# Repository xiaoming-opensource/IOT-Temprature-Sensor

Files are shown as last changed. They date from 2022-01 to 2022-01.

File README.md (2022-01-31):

# 小明开源-物联网温度贴
#采用超小体积BLE和WIFI双模SOC芯片
#完全开源，包括硬件原理图，PCB，外壳，嵌入式源代码等所有

##点击观看视频介绍>>
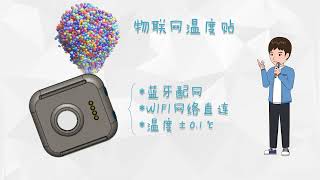
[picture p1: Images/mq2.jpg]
Watch the video (https://youtu.be/xRjZt0CQz3k)


#功能特点如下：

#量度温度，可达医疗级
Medical Level for Measurement of Temperature	
与医疗仪器比较±0.1度摄氏
±0.1℃ compared with Medical Instruments

#通讯功能
Communication	
低功耗WiFi 自动联网
Low Consumption to connect nearby WiFi Automatically
实时数据独立上传
Real Time Transmission

#定位
Location	
佩戴者地点定位
Positioning & Location of the Wearer

#电源
Power Source	
锂电池，可用48小时、磁吸充电
Lithium Battery by Magnetic Charging for use in 48 hours

#后台及小程序
Platform & Applets
实时数据监测
Real Time Data Monitoring
温度异常预警
Alerts of Abnormal Temperatures
实时数据一键分享多人
One-click Sharing of Real Time Data to Unlimited No. of People

#开发环境

#硬件设计
KiCAD
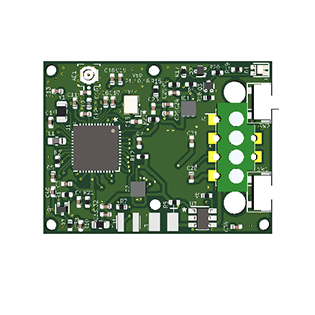
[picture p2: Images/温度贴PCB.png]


#软件设计
Keil uVision5

#外壳设计
Solidworks 2018

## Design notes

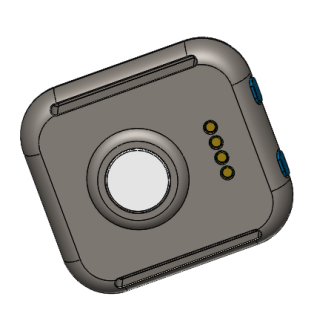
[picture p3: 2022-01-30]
Images/温度贴反面.png

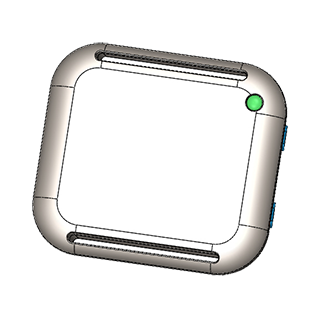
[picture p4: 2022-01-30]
Images/温度贴正面.png

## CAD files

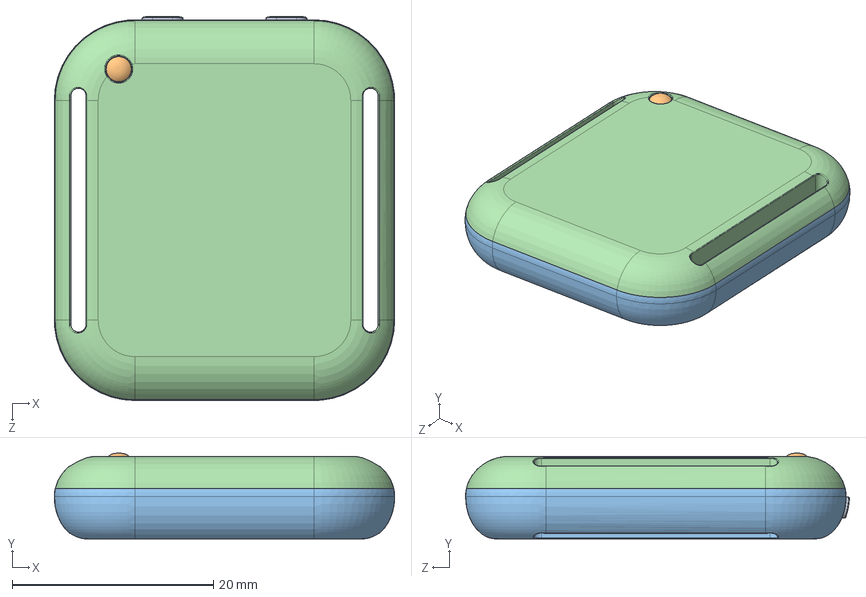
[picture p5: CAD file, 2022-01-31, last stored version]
MechanicalCase/case_v31mz.SLDASM
33.8 x 8.51 x 38.1 mm
button2v30
LED_POLE
body_v31
body_top_v31
battery202025
防水密封圈
popgo_pin_set
IOT-PCBA-v31
top_PAD

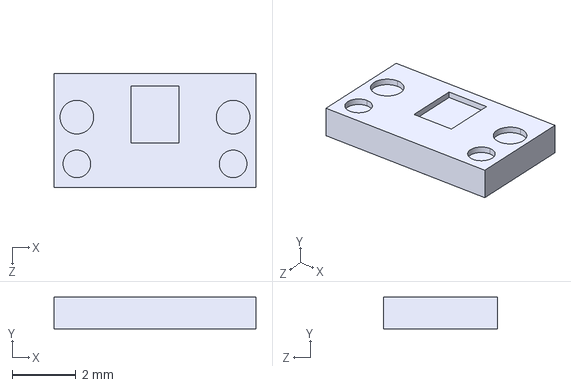
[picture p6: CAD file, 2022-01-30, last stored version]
Hardware/pah8011.STEP
6.36 x 1.00 x 3.60 mm

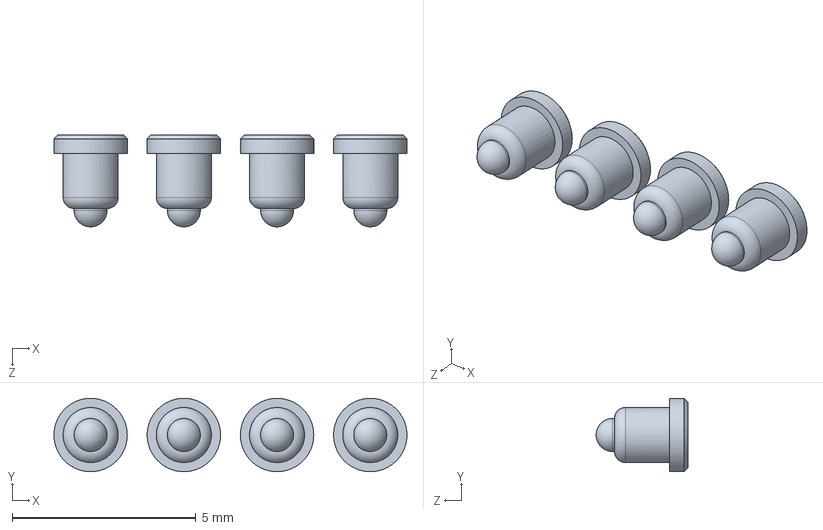
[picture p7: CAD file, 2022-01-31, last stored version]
MechanicalCase/popgo_pin_set.SLDPRT
9.62 x 2.00 x 2.50 mm

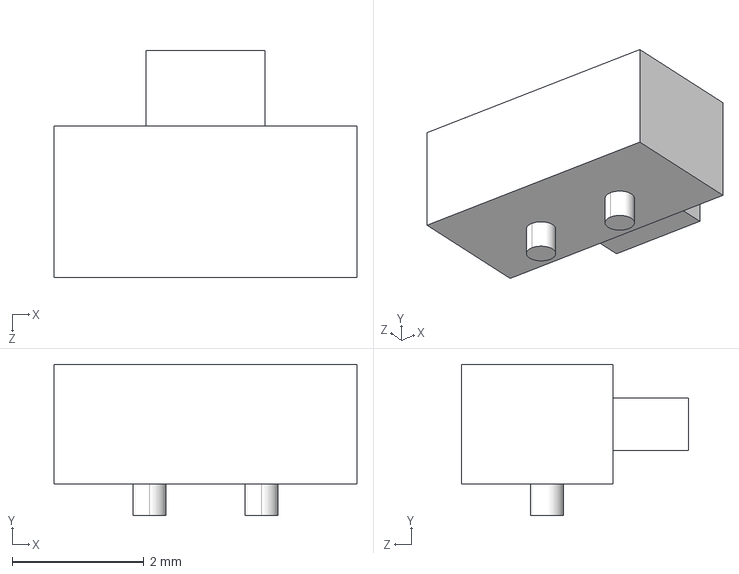
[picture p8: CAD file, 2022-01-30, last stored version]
Hardware/SOS_button.STEP
4.60 x 2.30 x 3.45 mm

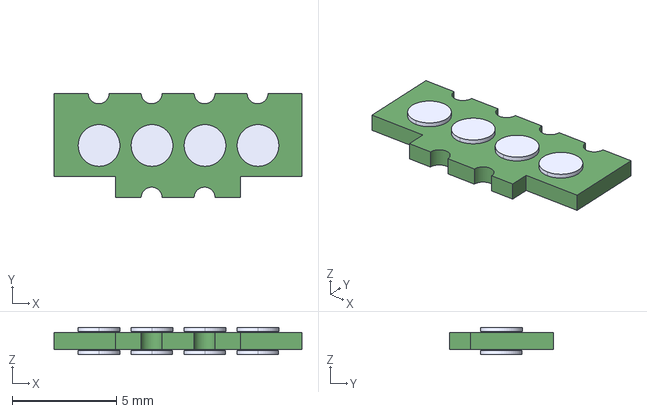
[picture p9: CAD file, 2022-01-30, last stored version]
Hardware/USB_charger.step
11.9 x 5.00 x 1.30 mm

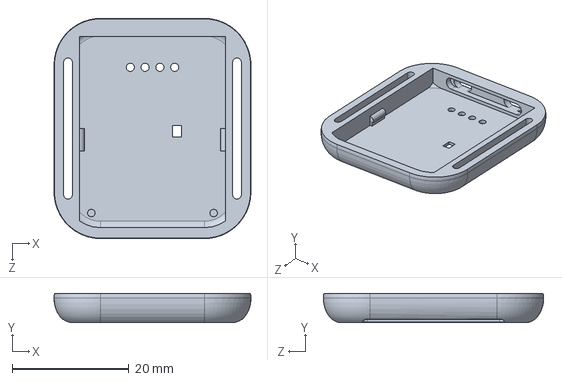
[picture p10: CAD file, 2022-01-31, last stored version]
MechanicalCase/body_v31.SLDPRT
33.8 x 5.00 x 37.8 mm

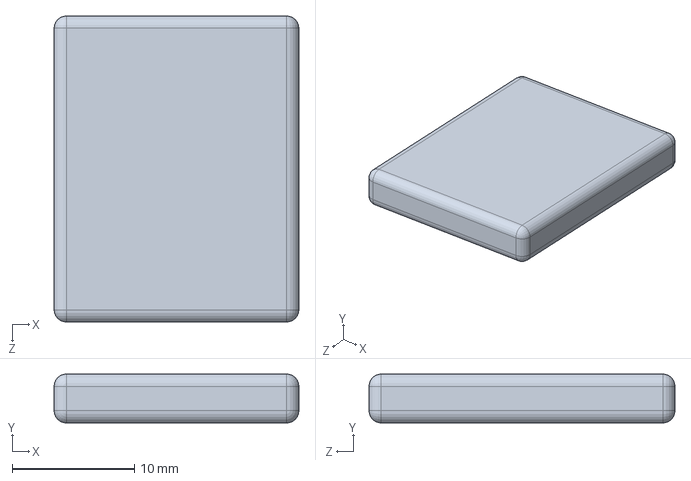
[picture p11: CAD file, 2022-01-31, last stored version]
MechanicalCase/battery202025.SLDPRT
20.0 x 4.00 x 25.0 mm

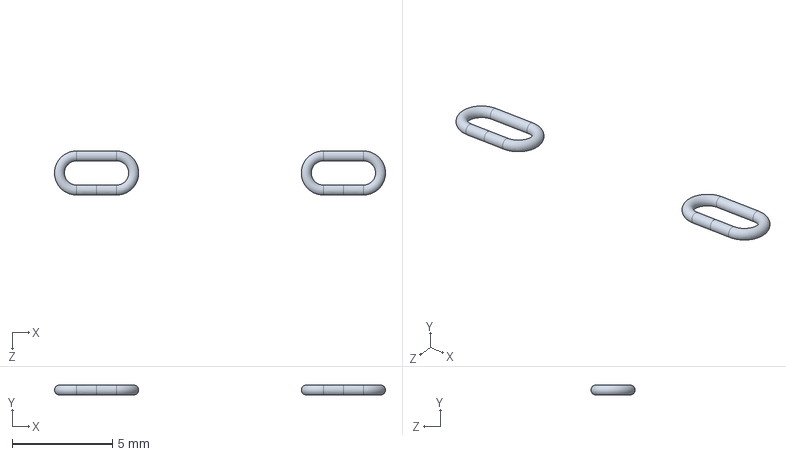
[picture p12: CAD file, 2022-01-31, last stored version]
MechanicalCase/防水密封圈.SLDPRT
16.5 x 0.5 x 2.20 mm

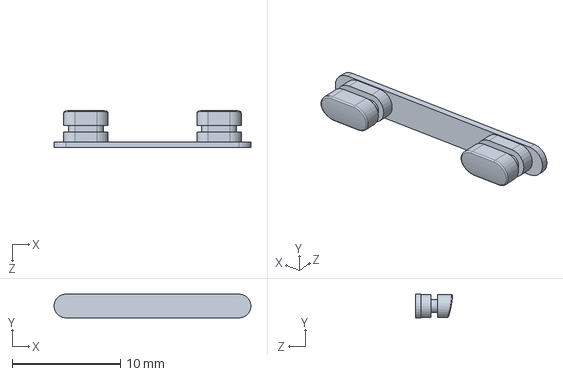
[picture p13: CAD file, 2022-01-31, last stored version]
MechanicalCase/button2v30.SLDPRT
18.2 x 2.20 x 3.43 mm

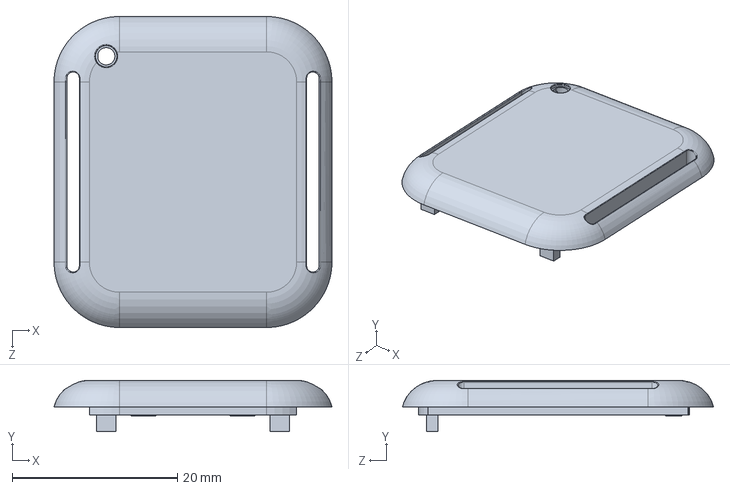
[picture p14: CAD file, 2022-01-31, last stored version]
MechanicalCase/body_top_v31.SLDPRT
33.6 x 6.20 x 37.6 mm

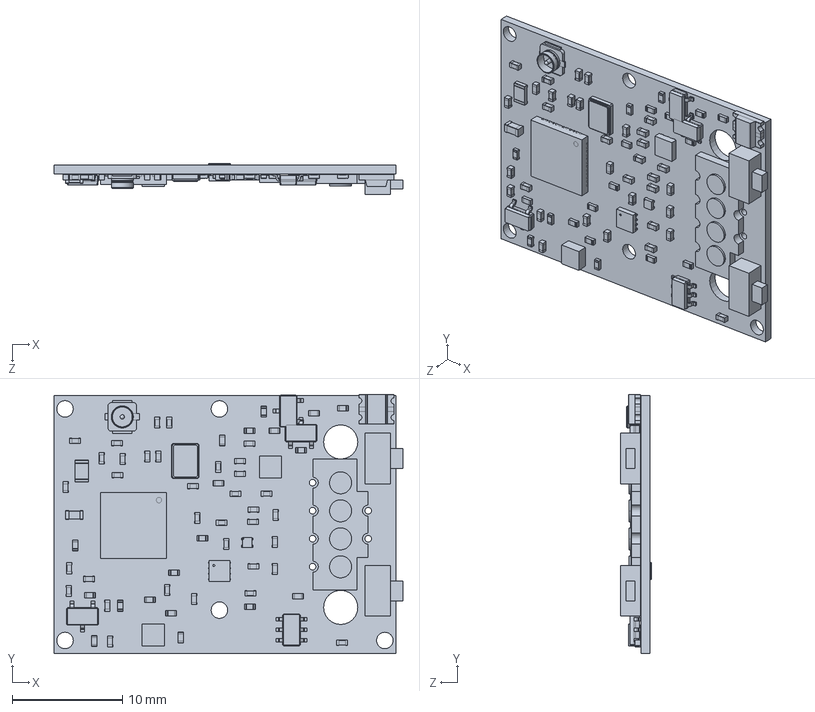
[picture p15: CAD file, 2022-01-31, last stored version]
MechanicalCase/IOT-PCBA-v31.SLDPRT
31.6 x 23.5 x 2.82 mm

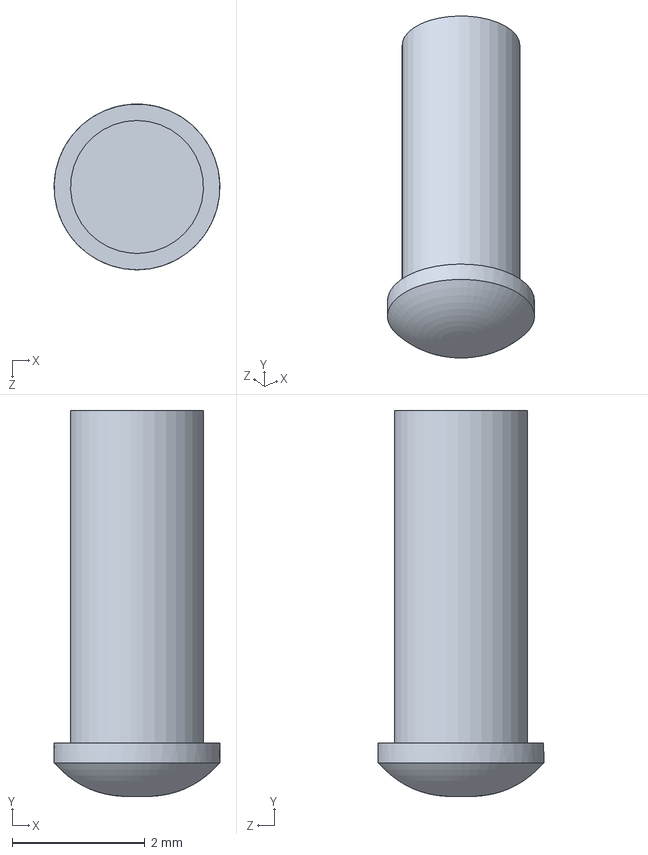
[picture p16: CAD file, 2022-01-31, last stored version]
MechanicalCase/LED_POLE.SLDPRT
2.49 x 5.81 x 2.49 mm

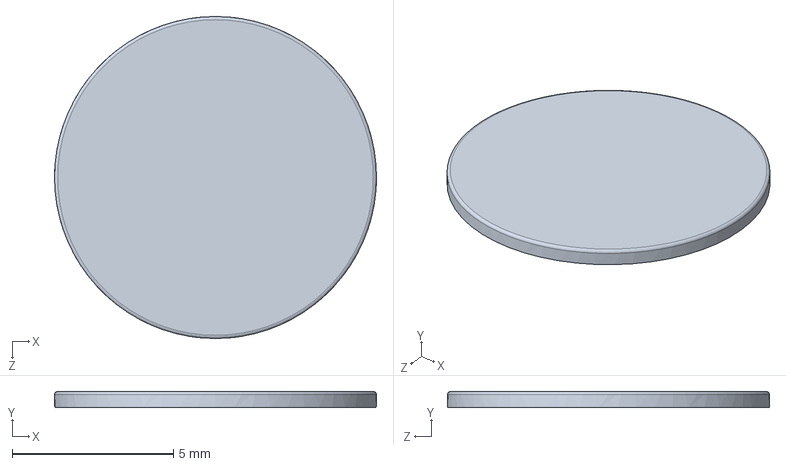
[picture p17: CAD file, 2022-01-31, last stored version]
MechanicalCase/top_PAD.SLDPRT
10.0 x 0.5 x 10.0 mm

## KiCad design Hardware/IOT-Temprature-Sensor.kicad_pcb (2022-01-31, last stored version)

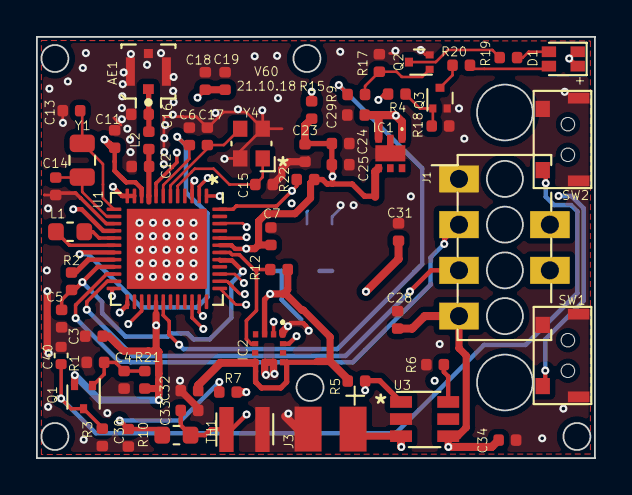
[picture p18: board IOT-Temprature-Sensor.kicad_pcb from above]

Board: 4 copper layers, 31.0 x 23.4 mm, 60 parts (0 on the bottom side), 40 nets.

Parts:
AE1: Antenna; 20449-001E-V2
C3, C18, C25, C31, C32: 0.1uF; C_0402_1005Metric
C4, C23: 10nF; C_0402_1005Metric
C5, C6, C7, C11, C19, C40: 4.7uF; C_0402_1005Metric
C12: 1.5pF; C_0402_1005Metric
C13, C14: 12pF; C_0402_1005Metric
C15, C17: 15pF; C_0402_1005Metric
C16: 0.5pF; C_0402_1005Metric
C24, C29, C34: 10uF; C_0402_1005Metric
C28, C30, C33: 1uF; C_0402_1005Metric
D1: LED_Dual_AACC; LED_RGBA_0606
IC1: AP7366-33SN-7; AP7366SN7
IC2: BMA423
J1: Conn_01x04_Male; usb_charger_6_pins
J3: Conn_01x02; BATTERY_CON2
L1: BRL1608T4R7M; L_0603_1608Metric
L2: 4.7nH; L_0402_1005Metric
Q1: CJE3139K; SOT-523
Q2, Q3: MMBT3904; SOT-723
R1: 3.9M; R_0402_1005Metric
R2: 0R; R_0402_1005Metric
R3: 10M; R_0402_1005Metric
R4, R9: 4.7K; R_0402_1005Metric
R5, R21: 680K; R_0402_1005Metric
R6: 1.2K; R_0402_1005Metric
R7, R17, R18: 47K; R_0402_1005Metric
R10: 20K 0.1%; R_0603_1608Metric
R12, R15, R22: 10K; R_0402_1005Metric
R19, R20: 2.2K; R_0402_1005Metric
SW1, SW2: SW_1003B; 1TS003B4PIN
TH1: Thermistor_NTC; NTC_RES
U1: OPL1200; UQFN-48-1EP_6x6mm_P0.4mm_EP4.45x4.45mm
U3: TP4057X; TSOT-23-6
Y1: 32.768KHZ; R_0805_2012Metric
Y4: 22MHZ; Crystal_SMD_Abracon_ABM10-4Pin_2.5x2.0mm

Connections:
+3V3: C3.1, C7.1, C11.1, C23.1, C24.1, C25.1, C31.2, C32.1, D1.1, D1.2, IC1.4, IC2.3, IC2.7, IC2.10, Q1.2, R5.1, R12.1, R15.1, R21.1, R22.1, U1.10, U1.16, U1.29, U1.43
+BATT: C29.1, IC1.1, IC1.3, J3.2, R7.1, U3.3
/ALT_LED: R9.1, U1.30
/ALT_LED_RED: R4.1, U1.44
/DBG_RX: J1.3, U1.23
/DBG_TX: J1.2, U1.22
/DCDC_IN: C6.1, U1.7, U1.19
/EN: C40.1, Q1.3, R3.1, SW2.1, U1.11, U1.12
/FLASH_MISO: U1.1, U1.39
/FLASH_MOSI: U1.2, U1.38
/FLASH_SCLK: U1.3, U1.37
/GPIO5_ADC5: C33.1, R10.1, TH1.1, U1.27
/GPIO17: IC2.5, R12.2, U1.42
/GPIO22: R22.2, U1.48
/I2C_SCL: IC2.12, U1.34
/I2C_SDA: IC2.2, U1.35
/ISCHRG: R5.2, U1.24, U3.1
/SOS_KEY: R15.2, SW1.1, U1.46
/VDD: C5.1, R2.2, U1.21, U1.41
/VDD_RF: C18.1, C19.1, U1.8
/VOLT_TP: C30.1, R7.2, R10.2, U1.25
GND: AE1.2, C3.2, C4.2, C5.2, C6.2, C7.2, C11.2, C12.2, C13.2, C14.1, C15.2, C16.2, C17.1, C18.2, C19.2, C23.2, C24.2, C25.2, C28.2, C29.2, C30.2, C31.1, C32.2, C33.2, C34.2, C40.2, IC1.2, IC1.7, IC2.1, IC2.8, IC2.9, J1.1, J3.1, Q2.2, Q3.2, R1.2, R3.2, R6.2, R17.1, R18.1, SW1.2, SW1.3, SW1.4, SW2.2, SW2.3, SW2.4, TH1.2, U1.15, U1.49, U3.2, Y4.2, Y4.4
unnamed: AE1.1, C16.1, L2.1
unnamed: C4.1, Q1.1, R1.1, R21.2
unnamed: C12.1, L2.2, U1.9
unnamed: C13.1, U1.13, Y1.1
unnamed: C14.2, U1.14, Y1.2
unnamed: C15.1, U1.5, Y4.1
unnamed: C17.2, U1.6, Y4.3
unnamed: D1.3, R20.2
unnamed: D1.4, R19.2
unnamed: L1.1, U1.18
unnamed: L1.2, U1.17
unnamed: Q2.1, R9.2, R17.2
unnamed: Q2.3, R19.1
unnamed: Q3.1, R4.2, R18.2
unnamed: Q3.3, R20.1
unnamed: R2.1, U1.20
unnamed: R6.1, U3.6
VBUS: C28.1, C34.1, J1.4, U3.4
